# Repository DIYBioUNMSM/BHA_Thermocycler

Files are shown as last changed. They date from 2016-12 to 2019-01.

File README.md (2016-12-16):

#BHA Thermocycler

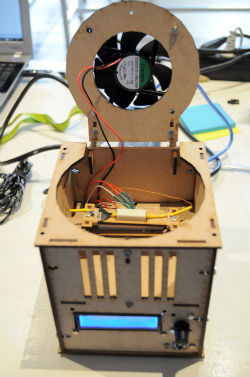
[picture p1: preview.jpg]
DIY Thermocycler
This repo contains the designs and source files of a **DIY Thermocycler**. This device can be used to perform a polymerase chain reaction on DNA. Check out the corresponding [BHA lecture in the Syllabus](http://biohackacademy.github.io) for more information.

##Navigating the repo

 	BHA_Thermocyler/					main repo
 	|-- Arduino Code/Thermocycler/		Arduino Code
 	|-- Assembly/						Electronics assembly guide
 	|-- Pictures/						Photo documentation
 	BoM.md								Bill of Materials
 	Thermocycler-Cut-Sheet-Nested.svg	Nested laser cut vector file
 	Thermocycler-Cut-Sheet.svg			Laser cut vector file
 	Thermocycler-Fritzing.fzz			Wiring Scheme
 	Thermocycler-Sketchup.skp			Sketchup 3D design
 	
##Releases

The BioHack Academy 3 release contains the following:

* 2015 BHA1 Design
* 2015 BHA2 Design
* 2016 BHA3 Design

## To Do

The To Do's are tracking using the Issues section of this GitHub Repo.

Please make more suggestions by posting there.

## License

All code is licensed under GNU General Public License.

All designs are licensed under Creative Commons Contribution Share-Alike license

Copyright Waag Society

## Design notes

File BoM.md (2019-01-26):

## Bill of Materials

Make sure you have an Arduino Leonardo or equivalent microprocessor. Also get enough 3mm material to cut the parts from and a bunch of M3 10mm bots and nuts.

### Components that are needed without using a Biohack Board

|No|Amount|Description|Supplier NL|Cost|
| ------------: | ------------: | :------------ | :------------ | ------------: |
|1|2|Power resistors|[Farnell](http://nl.farnell.com/webapp/wcs/stores/servlet/ProductDisplay?catalogId=15001&langId=31&urlRequestType=Base&partNumber=1292531&storeId=10168)|0.59|
|2|2|10K NTC thermistor| [Farnell](http://nl.farnell.com/avx/nd06p00103k/thermistor-ntc-10kohm-10-radial/dp/1672384), [HackerStore](https://www.hackerstore.nl/Artikel/156), [iPrototype](https://iprototype.nl/products/components/sensors/thermistor)|0.30|
|3|1|Rotary encoder|[Farnell](http://nl.farnell.com/alps/ec12e1240406/encoder-vertical-12mm-12det-12ppr/dp/2065052), [iPrototype](https://iprototype.nl/products/components/buttons-switches/rotary-encoder), [EOO](https://www.eoo-bv.nl/encoder-potmeter/9553-enc-potm-24p-xxx.html)|0.65|
|4|1|Knob|[Farnell](http://nl.farnell.com/multicomp/cr-r4-7/knob-soft-touch-d-shaft-black/dp/1440012?ost=1440012)|0.73|
|5|1|Power switch|[Farnell](http://nl.farnell.com/webapp/wcs/stores/servlet/ProductDisplay?catalogId=15001&langId=31&urlRequestType=Base&partNumber=4710368&storeId=10168), [iPrototype](https://iprototype.nl/products/components/buttons-switches/rocker-switch-large)|1.01|
|6|1|DC power jack|[Farnell](http://nl.farnell.com/multicomp/jr1819-rohs-psg01769/socket-low-voltage-2-1mm-chassis/dp/1216726), [EOO](https://www.eoo-bv.nl/voeding-dc/14342-v-c-2mm1-moer-lc.html)|0.85|
|7|1|12V 5A Power supply|[OnlineKabelShop](https://www.onlinekabelshop.nl/voedingsadapter-12v-5a-60w-5-5mm-x-2-5mm-voor-o-a-monitoren-van-diverse-merken?channable=e17871.NDQ1MTA&gclid=EAIaIQobChMIhd7Qx8yM4AIVD-WaCh22YwrCEAQYBCABEgJjqPD_BwE)|19.99|
|8|1|Push button|[Farnell](http://nl.farnell.com/omron-electronic-components/b3f4155/switch-projected-12x12x7-3-260gf/dp/1960977?ost=OMRON+ELECTRONIC+COMPONENTS++B3F4155&selectedCategoryId=&categoryNameResp=Alle%2Bcategorie%25C3%25ABn&searchView=table&iscrfnonsku=false),[iPrototype](https://iprototype.nl/products/components/buttons-switches/pcbbutton)|0.42|
|9|4|10K resistor|[Farnell](http://nl.farnell.com/te-connectivity/cfr16j10k/resistor-carbon-10k-0-25w-5/dp/2329474), [EOO](https://www.eoo-bv.nl/metaaloxide-1w/7016-metaalox-1w-10k.html)|0.03|
|10|4|Rubber feet|[Conrad](https://www.conrad.nl/nl/toolcraft-elastische-buffer-zelfklevend-pd2104sw-x-h-10-mm-x-4-mm-zwart-1-stuks-401489.html)|0.08|
|11|1|I2C LCD display|[iPrototype](https://iprototype.nl/products/components/led-lcd/lcd16x2-I2C-BL), [Hackerstore](https://www.hackerstore.nl/Artikel/82)|8.95|
|12|3|MOSFET|[Farnell](http://nl.farnell.com/stmicroelectronics/stp36nf06l/mosfet-n-logic-to-220/dp/9935614?CMP=i-bf9f-00001000), [EOO](https://www.eoo-bv.nl/mosfets-to-220-tm-100v/1279-buz11.html)|0.60|
|13|1|12V 80 mm Axial Fan|[Farnell](http://nl.farnell.com/bisonic/sp802512l-03/fan-80x25mm-12vdc/dp/1832326), [EOO](https://www.eoo-bv.nl/ventilatoren-fan/13244-ee80251s3.html)|3.35|
|14|1|Diode|[Farnell](http://nl.farnell.com/on-semiconductor/1n4004rlg/rectifier-1a-400v-axial/dp/2533160), [iPrototype](https://iprototype.nl/products/components/overige/diode), [EOO](https://www.eoo-bv.nl/1500w-diode/10717-15ke30a.html)|0.19|
|15|1|Breadboard|[Farnell](http://nl.farnell.com/pro-signal/psg-bb-400/breadboard-400-pin-white/dp/2503765). [iPrototype](https://iprototype.nl/products/accessoires/breadboards-prints/halfbreadboard)|2.56|
|16|1|Custom milled PCR tube block|||

*Estimate total*: EUR 40.55 (*excluding the aluminium block*)

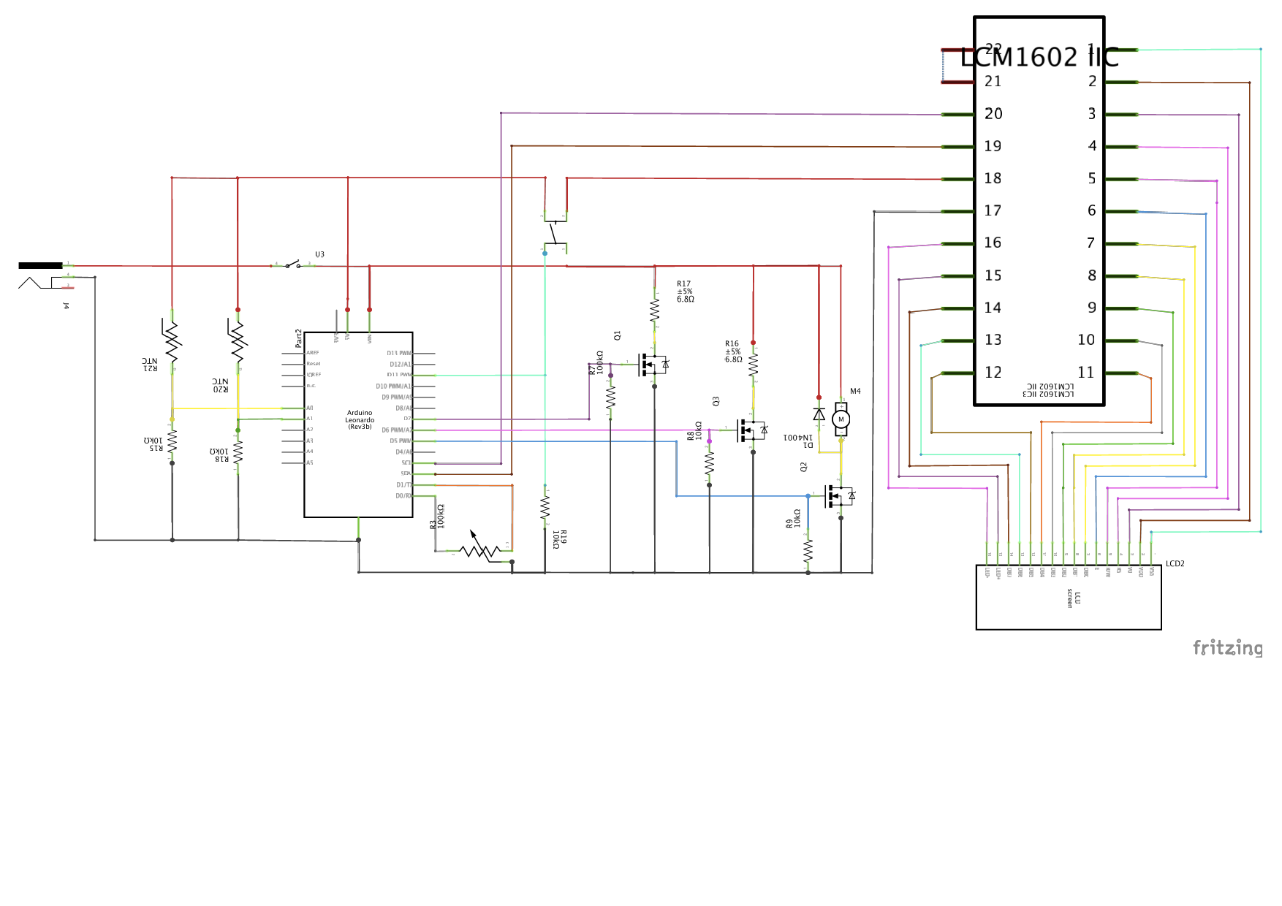
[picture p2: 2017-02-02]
Thermocycler-Schematic.png

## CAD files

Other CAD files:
Thermocycler-Sketchup.skp

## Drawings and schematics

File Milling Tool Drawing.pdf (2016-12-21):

## Drill for Eppendorf PCR Tube 0.2 ml

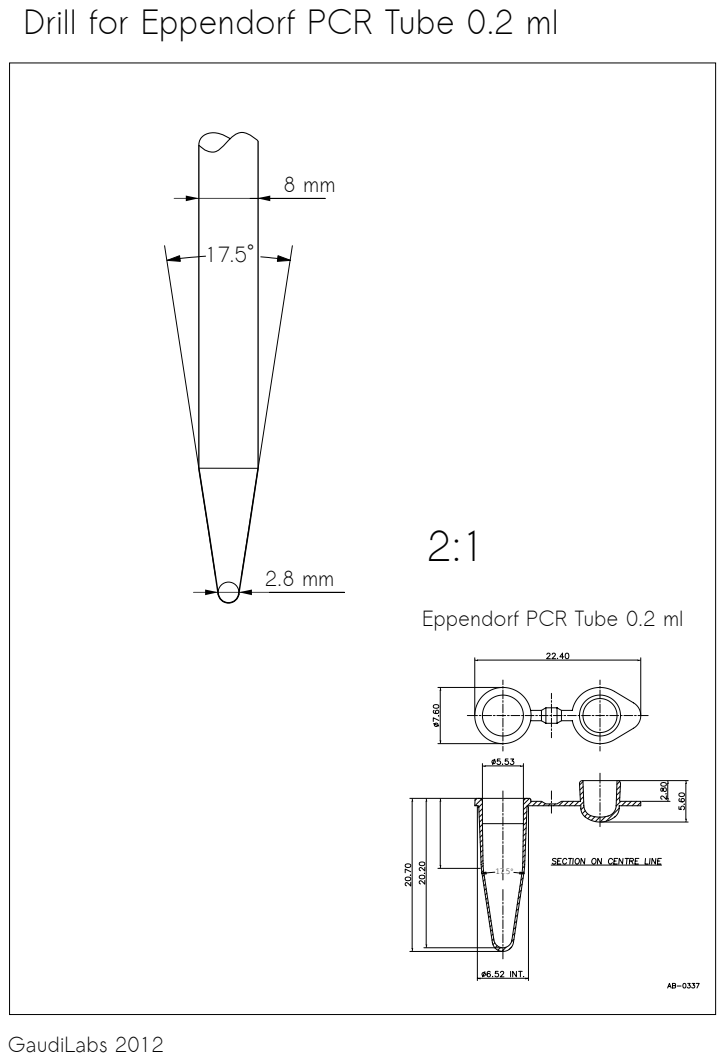
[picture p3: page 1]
GaudiLabs 2012

Eppendorf PCR Tube 0.2 ml

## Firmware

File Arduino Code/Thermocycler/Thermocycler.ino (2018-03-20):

/*
	This file is part of Waag Society's BioHack Academy Code.

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
	You should have received a copy of the GNU General Public License
	along with Waag Society's BioHack Academy Code. If not, see 
	<http://www.gnu.org/licenses/>.


 PLEASE NOTE:

 The thermocycler is perhaps the most complex device in the BioHack
 Academy thus far. The logic of the code is explained in the lecture.
 Please make sure you understand the logic, before changing the code.

 Once again this code is intended to demonstrate the minimal functions
 of a thermocycler. The code is able to run through multiple cycles of
 3 stage (Denaturing, Annealing, Elongation) PCR cycles.
*/

boolean toggleLidHeater = false; // False = lid heater off, True = lid heater on
int lidTemp = 85;       // Target lid temp

int arduinoType = 0; // Choose: 0 = Arduino UNO; 1 = Arduino Leonardo
int tempSensorType = 0; // Choose: 0 = 10K NTC thermistor; 1 = DS18B20 digital temperature sensor

class RotaryEncoder
{
  byte state;
  byte pin0, pin1;
  int value;

  byte readState()
  {
    return (digitalRead(pin0) == HIGH ? 1u : 0u)
         | (digitalRead(pin1) == HIGH ? 2u : 0u);
  }
public:
  RotaryEncoder(int p0, int p1) :
    pin0(p0), pin1(p1), value(0), state(0) {}
  
  void init()
  {
    pinMode(pin0, INPUT);
    pinMode(pin1, INPUT);
    digitalWrite(pin0, 1);  // enable internal pullup
    digitalWrite(pin1, 1);  // enable internal pullup
    value = 0;
    state = readState();
  }

  bool poll()
  {
    // State transition table
    static char tbl[16] =
    { 0, +1, -1, 0,
      // position 3 = 00 to 11, can't really do anythin, so 0
      -1, 0, -2, +1,
      // position 2 = 01 to 10, assume a bounce, should be 01 -> 00 -> 10
      +1, +2, 0, -1,
      // position 1 = 10 to 01, assume a bounce, should be 10 -> 00 -> 01
      0, -1, +1, 0
      // position 0 = 11 to 10, can't really do anything
    };
  
    byte t = readState();
    char movement = tbl[(state << 2) | t];
    if (movement != 0)
    {
      value += movement;
      state = t;
      return true;
    }
    return false;
  }
  
  int getValue()
  {
    return value;
  }
};


/* *******************************************************
/  Libraries
*/

#include <math.h>   // loads a library with more advanced math functions
#include <Wire.h>   // Needed for I2C connection with LCD screen
#include "LiquidCrystal_I2C.h" // Needed for operating the LCD screen
#include <OneWire.h>// Needed for the temperature sensors
#include <DallasTemperature.h> // Temperature reading library
/* *******************************************************
*/

/* *******************************************************
/  LCD
*/
// Set the LCD address to 0x27 for a 16 chars and 2 line display
LiquidCrystal_I2C lcd(0x27,16,2);
/* *******************************************************
*/

/* *******************************************************
/  Thermocycler Settings
*/
String stageNames[3] = { "Denat", "Anneal", "Elon" }; // Names of Stages
int tempSettings[3] = { 0, 0, 0}; // Temperatures of each stage
int timeSettings[3] = { 0, 0, 0}; // Duration of each stage
int coolSettings[3] = { 1, 0, 0}; // Toggle to enable fan / cooling after stage (only after Denat stage)
int cycleSetting = 0;     // Max number of cycles

// Pins
#define fanPin 5       // The mosfet that drives the 80mm fan is connected to pin 6
#define heatPin 6      // Pin for the mosfet that controls the heating element
#define lidPin 7       // Pin for the mosfet that controls the lid heater

// Temperature read
int val;               // Create an integer variable to temporarily store the thermistor read
double currentTemp;    // Variable to hold the current temperature value
double currentLidTemp; // Variable to hold the current lid temperature value
#define TempPin1 9     // DS18S20 Signal pin on digital 9
#define TempPin2 10    // DS18S20 Signal pin on digital 10

// Setup a oneWire instance to communicate with any OneWire devices (not just Maxim/Dallas temperature ICs)
OneWire oneWire1(TempPin1);
OneWire oneWire2(TempPin2);

// Pass our oneWire reference to Dallas Temperature. 
DallasTemperature tempSensor1(&oneWire1);
DallasTemperature tempSensor2(&oneWire2);

// PCR cycling variables
int stageTemp = 0;      // Target temperature of the current stage
int stageTime = 0;      // Duration of current stage
int cycleCounter = 0;   // Counter of number of cycles completed
int currentState = 0;   // 3 states: Denat, Anneal and Elon
unsigned long currentStageStartTime = 0; // Beginning of the current Stage
int currentStage = 0;   // In each stage, go through 3 states: Ramping, Steady, Cooling
int toggleCooling = 0;  // Toggle to skip or execute Stage 3: Cooling
boolean showtime = false; // Display time on display

/* *******************************************************
*/

/* *******************************************************
/  Set the initial STATE of the machine
/  In this code we will switch operation modes, from (programming time, to programming temp) x3, to cycling, to stopping/slowing down
*/
#define STATE_DENAT_TIMEPROG 1
#define STATE_DENAT_TEMPPROG 2
#define STATE_ANNEAL_TIMEPROG 3
#define STATE_ANNEAL_TEMPPROG 4
#define STATE_ELON_TIMEPROG 5
#define STATE_ELON_TEMPPROG 6
#define STATE_CYCLESPROG 7
#define STATE_CYCLING 8
#define STATE_STOP 9

byte state = STATE_DENAT_TIMEPROG;
/* *******************************************************
*/

/* *******************************************************
/  Machine User Interface
*/
boolean buttonState = 0;    // Start button
boolean lastButtonState = false; // Debounce variable
long lastDebounceTime = 0;  // the last time the output pin was toggled
long debounceDelay = 500;    // the debounce time; increase if the output flickers
int ledstate = false;       // Blinking indicator LED

// Pins
#define buttonPin 11   // the number of the pushbutton pin
#define ledPin 13      // the number of Arduino's onboard LED pin
/* *******************************************************
*/

/* *******************************************************
/  Rotary Encoder
*/

volatile int lastEncoded = 0;
volatile long encoderValue = 0;

long lastencoderValue = 0;

int lastMSB = 0;
int lastLSB = 0;
/* *******************************************************
*/

/* *******************************************************
/  Variables needed for keeping track of time
*/
uint32_t lastTick = 0;  // Global Clock variable
int LCDTime = 0;        // Time tracker for LCD update

/* Useful Constants */
#define SECS_PER_MIN  (60UL)
#define SECS_PER_HOUR (3600UL)
#define SECS_PER_DAY  (SECS_PER_HOUR * 24L)
 
/* Useful Macros for getting elapsed time */
#define numberOfSeconds(_time_) (_time_ % SECS_PER_MIN)  
#define numberOfMinutes(_time_) ((_time_ / SECS_PER_MIN) % SECS_PER_MIN)
#define numberOfHours(_time_) (( _time_% SECS_PER_DAY) / SECS_PER_HOUR)
#define elapsedDays(_time_) ( _time_ / SECS_PER_DAY)  
/* *******************************************************
*/

#if arduinoType == 0 
    RotaryEncoder rotaryEncoderA (2,3);
#endif
#if arduinoType == 1
    RotaryEncoder rotaryEncoderA (0,1);
#endif

/* *******************************************************
/  Setup function, this code is only executed once
*/
void setup() {
  // Encoder pins
  rotaryEncoderA.init();
  
  // Update clock
  lastTick = millis();

  // Initialize I2C connection with the LCD screen
  Wire.begin();

  // Open serial connection with the computer and print a message
  Serial.begin(9600);
  Serial.println(F("BioHack Academy Thermocycler"));

  // initialize the LED pin as an output:
  pinMode(ledPin, OUTPUT);
  // initialize the pushbutton pin as an input:
  pinMode(buttonPin, INPUT);
  
  // rotary encoder as an input
  /*
  pinMode(encoderPin1, INPUT); 
  pinMode(encoderPin2, INPUT);
  digitalWrite(encoderPin1, HIGH); //turn pullup resistor on
  digitalWrite(encoderPin2, HIGH); //turn pullup resistor on
  //call updateEncoder() when any high/low changed seen
  //on interrupt 0 (pin 2), or interrupt 1 (pin 3) 
  attachInterrupt(0, updateEncoder, CHANGE); 
  attachInterrupt(1, updateEncoder, CHANGE);  */

  // fan and heating and set low
  pinMode(fanPin, OUTPUT);
  pinMode(heatPin, OUTPUT);
  pinMode(lidPin, OUTPUT);
  digitalWrite(fanPin, LOW);
  digitalWrite(heatPin, LOW);
  digitalWrite(lidPin, LOW);

  // Start up the temperature sensor library
  tempSensor1.begin();
  tempSensor2.begin();
  
  // Initialize the LCD and print a message
  lcd.init();
  lcd.backlight();
  lcd.clear();
  lcd.setCursor(0,0);
  lcd.print(F("BioHack Academy"));
  lcd.setCursor(0,1);
  lcd.print(F("Thermocycler"));
  delay(1000);
  lcd.clear();
}
/* *******************************************************
*/

/* *******************************************************
/  Thermistor function converts the raw signal into a temperature
/  NOTE: no longer used
*/
double Thermister(int RawADC) {  //Function to perform the fancy math of the Steinhart-Hart equation
  double Temp;
  Temp = log(((10240000/RawADC) - 10000));
  Temp = 1 / (0.001129148 + (0.000234125 + (0.0000000876741 * Temp * Temp ))* Temp );
  Temp = Temp - 273.15;              // Convert Kelvin to Celsius
  //Temp = (Temp * 9.0)/ 5.0 + 32.0; // Celsius to Fahrenheit - comment out this line if you need Celsius
  return Temp;
}
/* *******************************************************
*/

/* *******************************************************
/  Loop function, this code is constantly repeated
*/
void loop() {
  // Update clock
  uint32_t time = millis();     // current time since start of sketch
  uint16_t dt = time-lastTick;  // difference between current and previous time
  lastTick = time;
  
  // Poll rotary encoder
  if (rotaryEncoderA.poll()) {
    Serial.print("Encoder A: ");
    Serial.println(rotaryEncoderA.getValue());
    encoderValue = rotaryEncoderA.getValue();
  }

     val=analogRead(A0);            //Read the Analog port 0 and store the value in val
     currentTemp=Thermister(val);  //Runs the fancy math function on the raw analog value
     val=analogRead(1);            //Read the Analog port 1 and store the value in val
     currentLidTemp=Thermister(val);  //Runs the fancy math function on the raw analog value
    
  // Print temperature to computer via Serial
  Serial.print("Temperature: ");
  Serial.println(currentTemp);
  //Serial.print("Lid Temperature: ");
  //Serial.println(currentLidTemp);

  // Check whether the button is pressed using debounce timer
  int reading = digitalRead(buttonPin);

  if ((millis() - lastDebounceTime) > debounceDelay) {
    if (reading == 1) {
      buttonState = 1;
      lastDebounceTime = millis();
    }
  }
  else {
    buttonState = 0;
  }
  
  // Blink the LED, indicating that the Arduino is working
  if (ledstate == false) {
    digitalWrite(ledPin, HIGH); // turn LED on
    ledstate = true;
  }
  else {
    digitalWrite(ledPin, LOW); // turn LED off
    ledstate = false;
  }
  
  // Do machine logic
  machineUpdate(dt);
  
  // Reset button state
  buttonState = 0;

  // Wait 10 microsconds before restarting the loop
  delay(10);
}
/* *******************************************************
*/
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

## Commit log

2016-03-06 SVG export
    [Thermocycler.skp]
2016-03-17 Updated Wiring & Arduino code
    [Thermocycler-Fritzing.fzz]
2016-04-05 wiring of fan
    [Thermocycler-Fritzing.fzz]
2016-04-14 pin switch
2016-07-18 Updated design
    [Thermocycler.skp]
2016-07-27 Verbeteringen en laseren met zo min mogelijk materiaal
    [Complete_thermocycler.fzz, Thermocycler-Fritzing.fzz]
2016-07-27 temperature sensor fix
2016-07-28 Leonardo wiring
2016-07-28 Rotate LCD
    [Thermocycler.skp]
2016-07-28 introducing a toggle for the Lid Heater
2016-07-28 lower lid temperature
2016-07-29 updated debounce
    [Complete_thermocycler.fzz]
2016-07-29 longer clamp
    [Thermocycler.skp]
2016-07-30 after Teacher Bootcamp update
    [Complete_thermocycler.fzz, Thermocycler - 10K Thermistor.fzz, Thermocycler - DS18B20 digital temp sensors.fzz]
2016-07-30 Differentiate between analog and digital temperature sensors
2016-11-11 clean up old versions
    [Complete_thermocycler.fzz, Thermocycler.skp]
2016-12-16 BHA4 Update
    [Complete_thermocycler.fzz, Thermocycler - 10K Thermistor.fzz, Thermocycler - DS18B20 digital temp sensors.fzz, Thermocycler-Fritzing.fzz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]
2016-12-21 milling tool
2017-02-02 fix power jack connection
    [Thermocycler-Fritzing.fzz]
2017-02-02 fix i2c pins
    [Thermocycler-Fritzing.fzz]
2017-02-02 schematic done - pdf
    [Thermocycler-Fritzing.fzz]
2018-03-20 changes in the arduino code by Emma during BHA5, now temperature is constantly measuered.

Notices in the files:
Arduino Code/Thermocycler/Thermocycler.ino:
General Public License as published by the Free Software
